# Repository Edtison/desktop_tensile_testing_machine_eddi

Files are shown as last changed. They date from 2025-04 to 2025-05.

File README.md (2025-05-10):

# Desktop Tensile Testing Machine

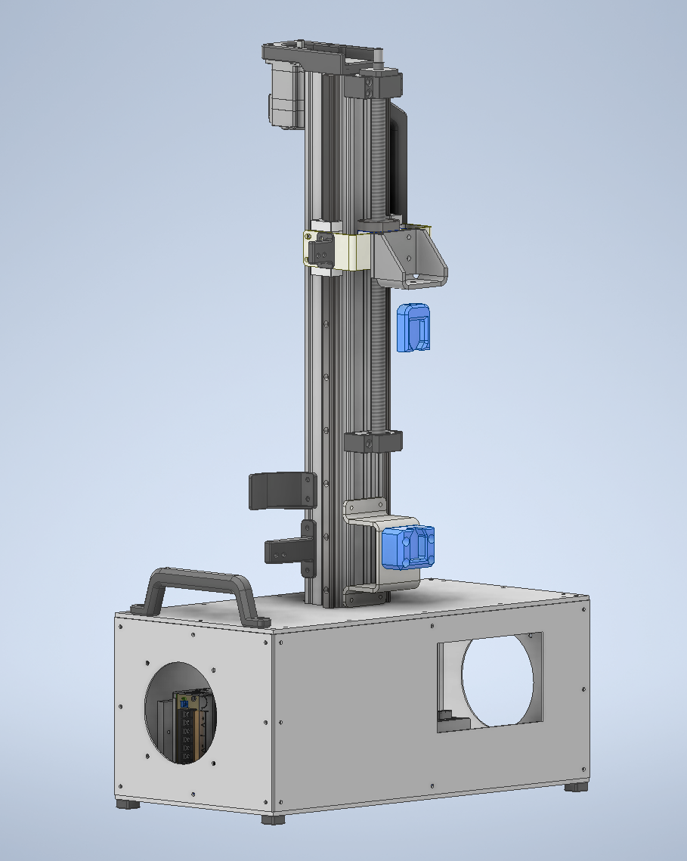
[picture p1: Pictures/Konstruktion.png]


## Overview

The tensile testing machine described here is a fully open-source device designed to determine the mechanical tensile strength of test specimens. At its core, it uses a single-board computer (typically a Raspberry Pi), which, in combination with a load cell and an HX711 amplifier, performs precise force measurements. A bipolar stepper motor module ensures defined positioning and feed control, enabling reproducible loading profiles.
The goal of the project is to provide an affordable and modular testing rig that can be used and further developed by both hobbyists and research laboratories. Control is provided via an intuitive touch GUI (based on ttkbootstrap and tkinter), which visualizes all relevant parameters—test length, feed rate, and force-drop threshold—in real time and automatically saves measurement data to CSV logs.
Thanks to the MIT open-source license, the entire source code is freely available on GitHub. The modular architecture and clear interfaces allow for customization, extensions, and the integration of additional sensors or actuators. This makes the tensile tester a flexible platform for material testing, educational purposes, and DIY projects.

Please Note: a good part of this project is made in german language

If you want to contribute please let me know 

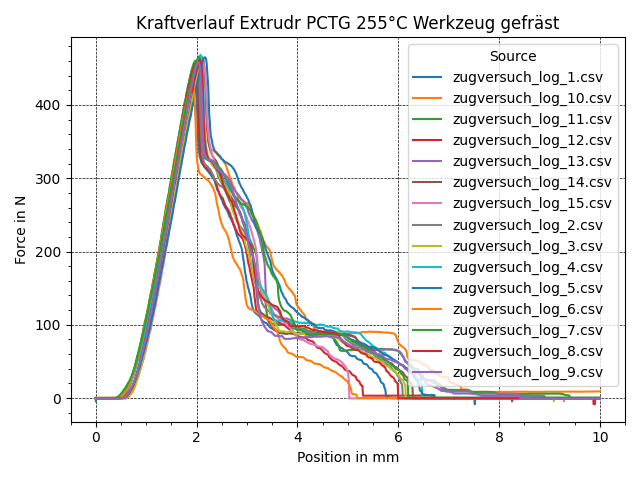
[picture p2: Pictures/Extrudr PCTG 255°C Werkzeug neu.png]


## Features

- **Precise Force Measurement**  
  Load cell with HX711 amplifier, tare & calibration routines.
- **Stepper Motor Control**  
  Configurable pull‑rate, travel distance, and emergency stop on force drop.
- **Intuitive Touch GUI**  
  Built with `ttkbootstrap` + `tkinter` for live feedback and parameter adjustment.
- **Automatic Logging**  
  CSV log files with position vs. force data, auto‑incrementing filenames.

## Requirements

- **Hardware**  
  - Raspberry Pi (5)  
  - HX711 load cell amplifier + load cell  
  - Bipolar stepper motor (Nema 23) + driver (enable, dir, step pins) (3,3V compatible) 
- **Software**  
  - Python 3.11 < 
  - MicroPython (for MCU variant)  
  - `gpiozero`  
  - `ttkbootstrap`  
  - `tkinter`

## Samples 

For good compareable data i would suggest you use the "sample typ cw" from this ropository. The infill should be 100%, the infill pattern rectalinear, with 2 wall loops. This will enshure you will get a homogeneous as possible infill as seen on th picture. Theres als a .3mf data in this repository you could use in Orca Slicer or "Anycubic next" Slicer. The sample contour is fetched from the ISO 20753, also to have good comparable data.

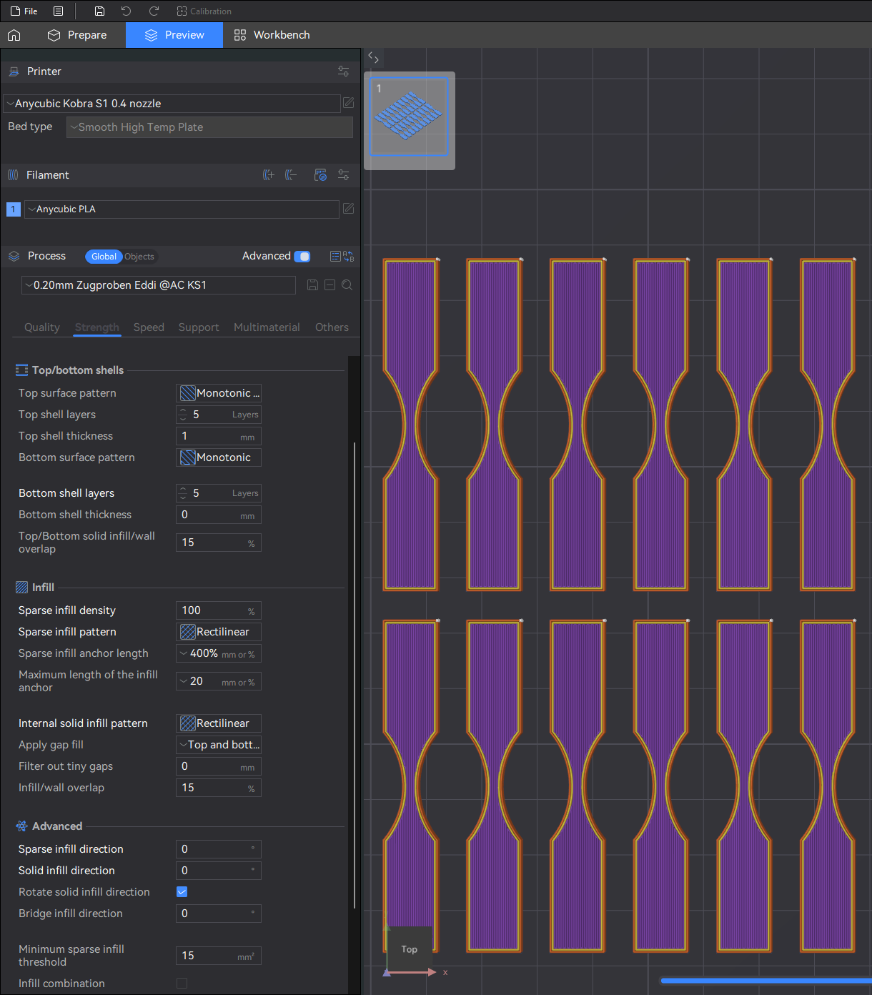
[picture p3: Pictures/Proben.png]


## Addition Milled Sample Holder (10.05.2025)

For a more consistant i've ordered a new sample holder milled from EN-AW7075 aluminum.
You will find the data to that in 3D files and CNC Milled Tool for Type CW

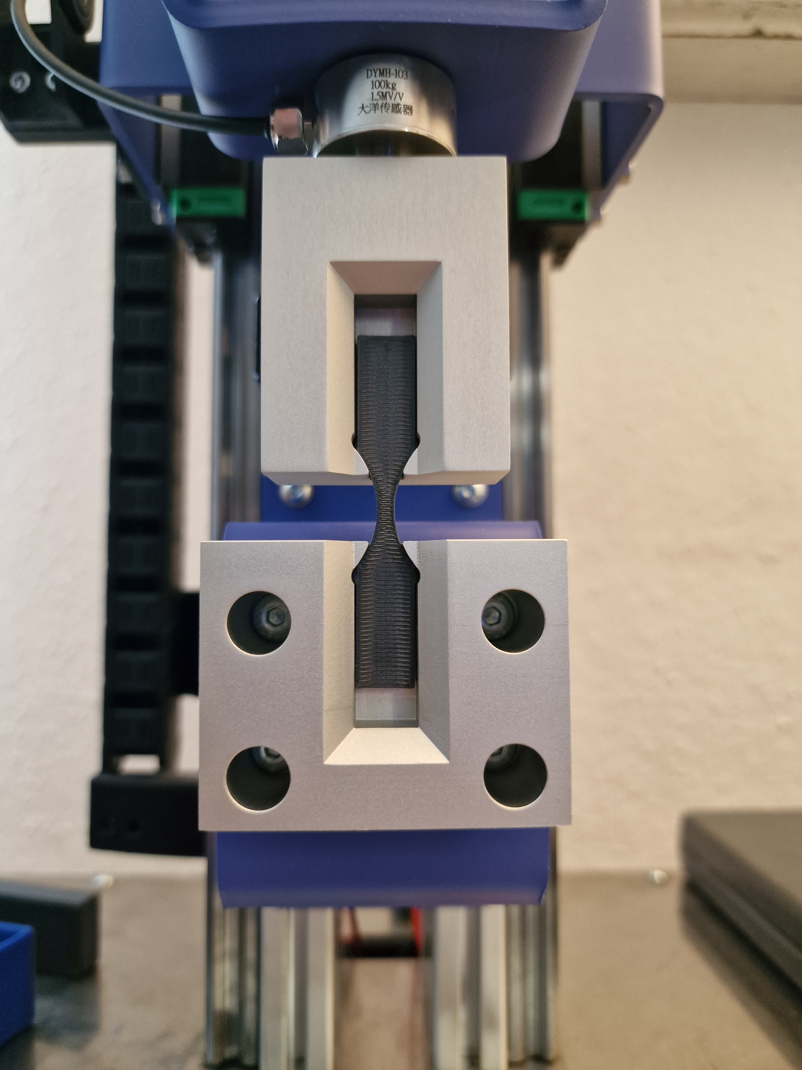
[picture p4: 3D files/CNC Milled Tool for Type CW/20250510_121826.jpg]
milled sample holder


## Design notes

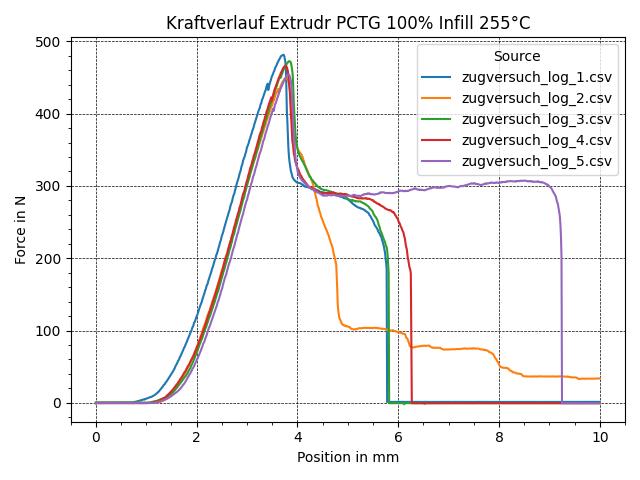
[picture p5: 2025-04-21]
Pictures/Diagram_Extrudr_PCTG.jpeg

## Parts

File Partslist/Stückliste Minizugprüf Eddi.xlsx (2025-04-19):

Stückliste Minizugprüfmaschine Eddi
ID | Bezeichnung | Shop / Firma | Menge | Preis Stk | Preis ges (N) | Preis ges (B) | Link
 | Profile
1 | Aluprofil 20x20 I-Typ Nut5 200mm | Motedis | 4 |  | 11.22 € | 13.46 €
2 | Aluprofil 20x20 I-Typ Nut5 210mm | Motedis | 4 |  | 3.38 € | 4.06 €
3 | Aluprofil 20x20 I-Typ Nut5 460mm | Motedis | 4 |  | 7.41 € | 8.89 €
4 | Aluprofil 20x60 I-Typ Nut5 600mm | Motedis | 2 |  | 27.07 € | 32.48 €
5 | Winkel 20 I-Typ Nut 5 | Motedis | 30 |  | 8.10 € | 9.72 €
6 | Nutenstein I Typ 5 M4 | Motedis | 100 |  | 17.00 € | 20.40 €
7 | Nutenstein mit Steg I-Typ Nut 5 [M5] | Motedis | 70 |  | 12.15 € | 14.58 €
8 | Energiekette 15x15 - 1m | Motedis | 1 |  | 3.80 € | 4.56 €
 | Linearbewegung
9 | 2Stück HGR20-600mm Führungsschiene mit 4Stück Hohe Präzision HGH20CA Linearlager Lagerblock, CNC Teile für 3D Drucker (linearführung HGR20 600mm) | Amazon | 1 |  |  | 48.46 € | https://www.amazon.de/dp/B09JFX8992?ref_=ppx_hzsearch_conn_dt_b_fed_asin_title_1
10 | SFU1605 Kugelumlaufspindel 450mm Gewindespindel Edelstahl Kugelumlaufspindel mit BK12/BF12 Unterstützung, | Amazon | 1 |  |  | 36.31 € | https://www.amazon.de/dp/B0B6RJPQDZ?ref_=ppx_hzsearch_conn_dt_b_fed_asin_title_1&th=1
 | Motor + Treiber
11 | 1 x 1 Achsen Schrittmotor CNC Kit 3,0Nm(425oz.in) Nema 23 Schrittmotor und Treiber | Stepperonline | 1 |  |  | 53.83 €
 | Elektronik
12 | 24V 5A 120W DC Schaltnetzteil AC 100V/240V auf DC-24V Netzteil | Amazon | 1 |  |  | 15.12 € | https://www.amazon.de/dp/B0BX2GF5QY?ref_=ppx_hzsearch_conn_dt_b_fed_asin_title_4
13 | YIMATEECO Staubfilter PC 120mm Lüfterabdeckungen für Computer-Kühlerlüfter | Amazon | 1 |  |  | 7.04 € | https://www.amazon.de/dp/B0BXJJH1X8?ref_=ppx_hzsearch_conn_dt_b_fed_asin_title_1&th=1
14 | LUCKFOX for Raspberry Pi Screen 7 inch HDMI Touchscreen for Raspberry Pi 5 | Amazon | 1 |  |  | 60.49 € | https://www.amazon.de/dp/B0CGNH5G68?ref_=ppx_hzsearch_conn_dt_b_fed_asin_title_1
15 | RPi GPIO Breakout-Erweiterungskarte + Flachbandkabel | Amazon | 1 |  |  | 5.64 € | https://www.amazon.de/dp/B07KB3JF68?ref_=ppx_hzsearch_conn_dt_b_fed_asin_title_3
16 | Raspberry Pi 5 4gb Ram | Berrybase | 1 |  |  | 65.90 € | https://www.berrybase.at/raspberry-pi-5-4gb-ram
17 | Raspberry Pi5 active Cooler | Berrybase | 1 |  |  | 5.70 € | https://www.berrybase.at/raspberry-pi-active-cooler-luefter-fuer-raspberry-pi-5
18 | HX711 Wägezelle 24-Bit-A/D-Wandlerchip für elektronische Präzisionswaage | Amazon | 1 |  |  | 7.04 € | https://www.amazon.de/dp/B07MY2PBY4?ref_=ppx_hzsearch_conn_dt_b_fed_asin_title_1
19 | DYMH 103 Mikro-Miniatur-Wägezelle Wägezelle Wägesensor Zugstangen-Druckspannungssensor (Bereich 0~100kg) | Amazon | 1 |  |  | 41.38 € | https://www.amazon.de/Mikro-Miniatur-W%C3%A4gezelle-W%C3%A4gezelle-W%C3%A4gesensor-Zugstangen-Druckspannungssensor-Bereich/dp/B0C3JFGVHX?__mk_de_DE=%C3%85M%C3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
20 | REV Standard, Feuchtraumsteckdose, Aufputz, grau | Amazon | 1 |  |  | 4.52 € | https://www.amazon.de/REV-Ritter-10216-Steckdose-Standard/dp/B00V3OI8YW
21 | 3 Stück Kaltgeräte Einbau-Stecker 220-250V/ 10A | Amazon | 1 | 10.07 € |  | 3.36 € | https://www.amazon.de/dp/B07T5D39R3?ref_=ppx_hzsearch_conn_dt_b_fed_asin_title_1
 | Blechteile
22 | Bodenplatte | Mon-Tec | 1 |  |  | 26.64 €
23 | Deckplatte | Mon-Tec | 1 |  |  | 29.78 €
24 | Festlagerblech | Mon-Tec | 1 |  |  | 29.89 €
25 | Führungswinkel | Mon-Tec | 2 | 11.35 € |  | 22.70 €
26 | Zugwinkel | Mon-Tec | 1 |  |  | 34.15 €
27 | Seitenblech | Mon-Tec | 2 | 15.00 € |  | 30.00 €
28 | Frontblech | Mon-Tec | 1 |  |  | 25.00 €
29 | Rückblech | Mon-Tec | 1 |  |  | 25.00 €
 | Schrauben
30 | M4x8 Inbus | Schraubenking | 100 |  |  | 2.45 €
31 | M4x10 Linsenflachkopf | Schraubenking | 100 |  |  | 2.64 €
32 | M5x12 Linsenflachkopf | Schraubenking | 30 |  |  | 0.90 €
33 | M5x16 Inbus | Schraubenking | 20 |  |  | 0.20 €
34 | Unterlegscheiben M4 | Schraubenking | 100 |  |  | 1.06 €
35 | Unterlegscheiben M5 | Schraubenking | 10 |  |  | 0.30 €
36 | M6 Mutter | Schraubenking | 1 |  |  | 0.00 €
 |  |  |  |  | Summe | 693.65 €
ID | 3D-Druck Teile | Menge
1 | Motorhalter Nema 23 | 1
2 | Halterung Kabelschlepp fahrend | 1
3 | Halterung Kabelschlepp fix | 1
4 | Tragegriff | 1
5 | Tragegriff seite | 1
6 | Auflage Kabelschlepp | 1
7 | Fliegender Probenhalter (auch als Frästeil möglich) | 1
8 | Probenhalter fix (auch als Frästeil möglich) | 1

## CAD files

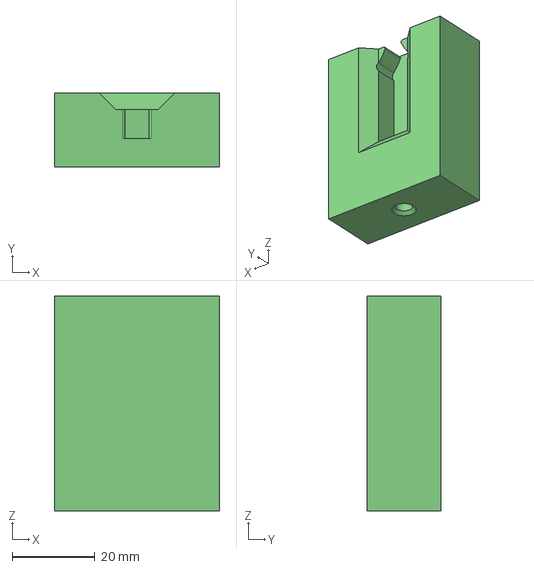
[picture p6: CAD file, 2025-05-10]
3D files/CNC Milled Tool for Type CW/Sample Holder flying CW.stp
40.0 x 18.0 x 52.0 mm

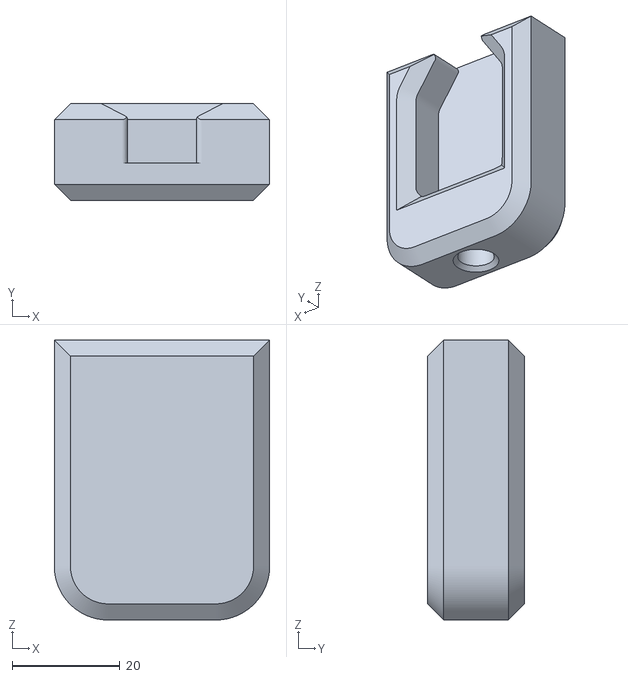
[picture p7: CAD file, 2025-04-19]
3D files/STL for printing/Fliegender Probenhalter.stl
40.0 x 18.0 x 52.0

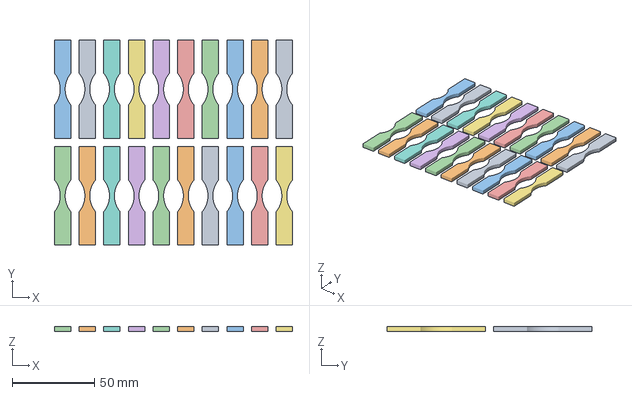
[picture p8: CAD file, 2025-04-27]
sample typ CW/sample Typ CW.3mf
145.0 x 125.0 x 3.00 mm
Zugprobe Typ CW.stl x 20

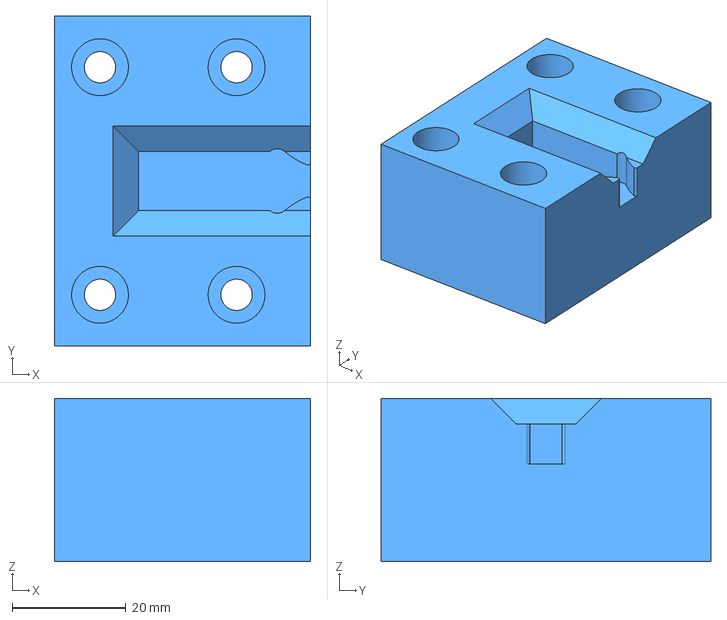
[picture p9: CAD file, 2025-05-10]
3D files/CNC Milled Tool for Type CW/Sample holder fixed CW.stp
45.0 x 58.0 x 28.7 mm

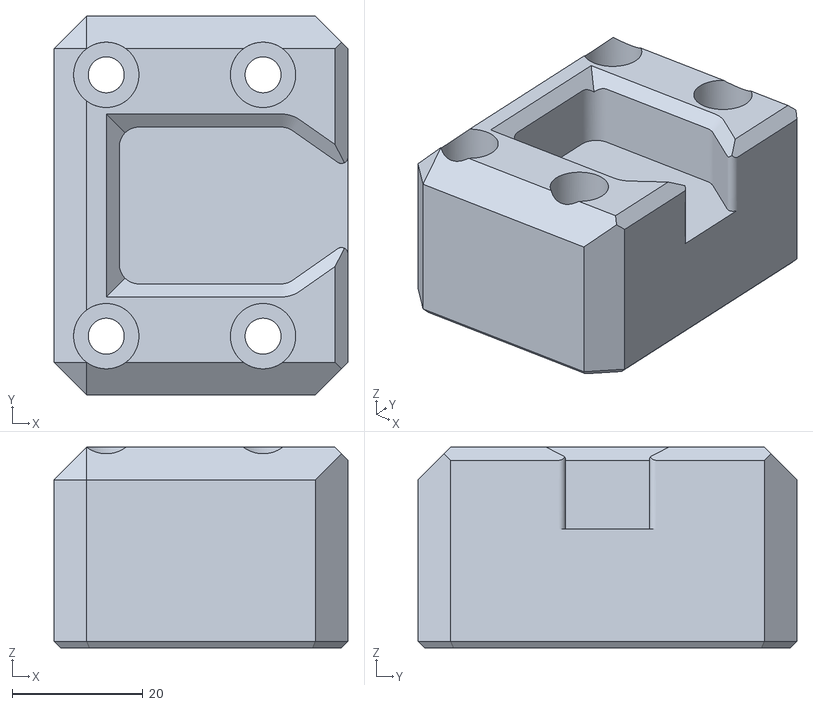
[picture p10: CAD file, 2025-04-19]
3D files/STL for printing/Probenhalter Fix.stl
45.0 x 58.0 x 30.7

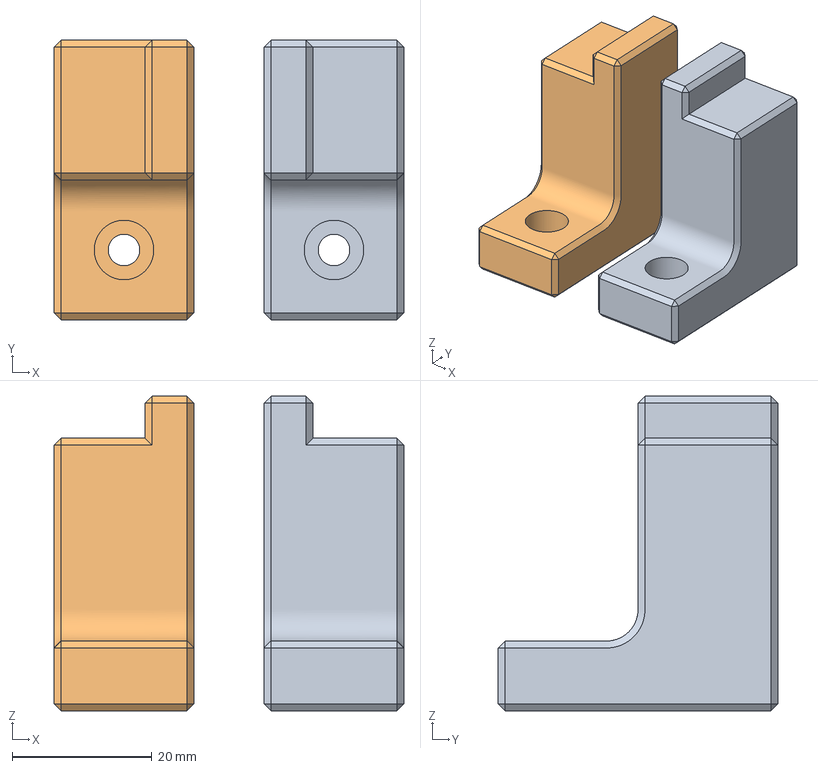
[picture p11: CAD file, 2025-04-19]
3D files/STL for printing/Bildschirm Steher.3mf
50.0 x 40.0 x 45.0 mm
Bildschirm Steher.stl x 2

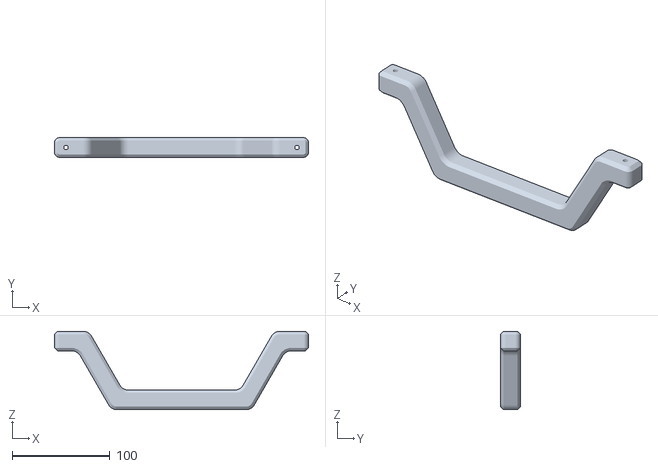
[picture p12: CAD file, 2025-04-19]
3D files/STL for printing/Tragegriff.stl
259.3 x 20.0 x 80.0

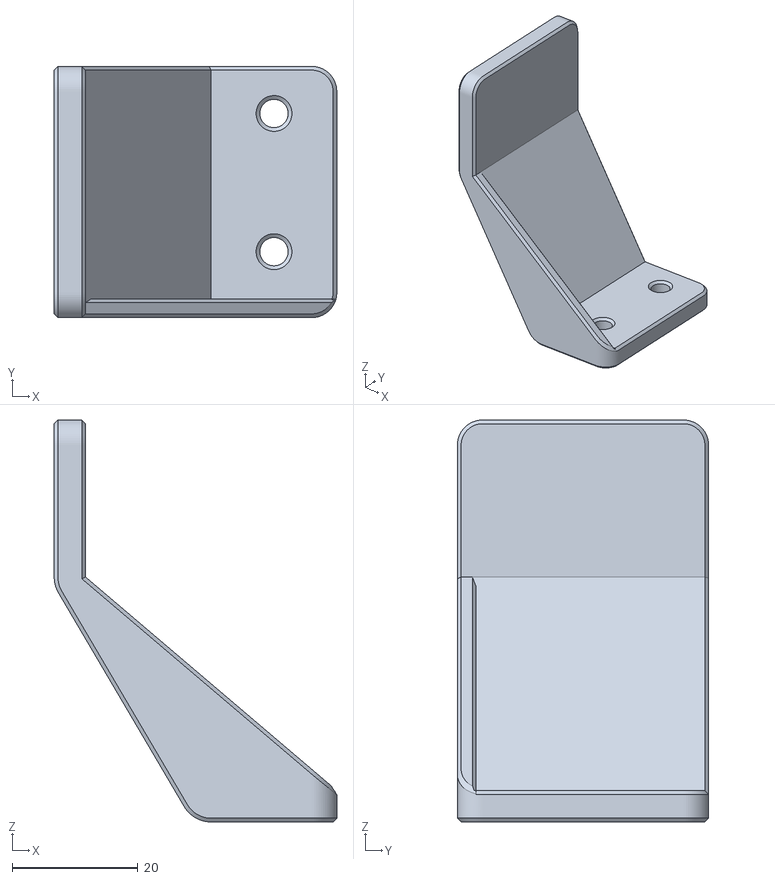
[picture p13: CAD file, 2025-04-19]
3D files/STL for printing/Auflage Kabelschlepp.stl
45.0 x 40.0 x 64.0

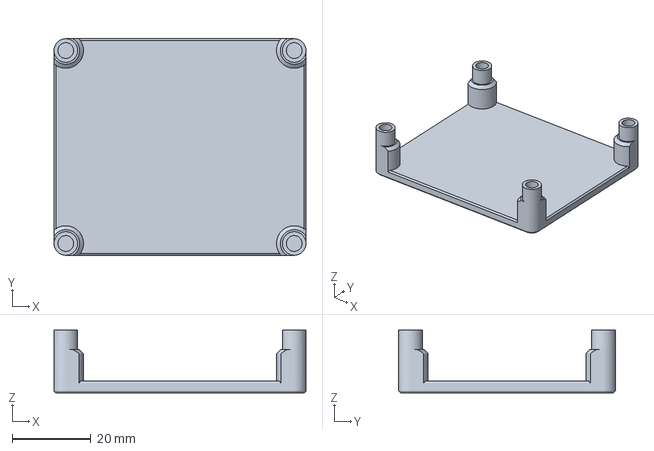
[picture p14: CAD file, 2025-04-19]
3D files/STL for printing/Raspberry Halterung.3mf
64.0 x 55.0 x 16.0 mm

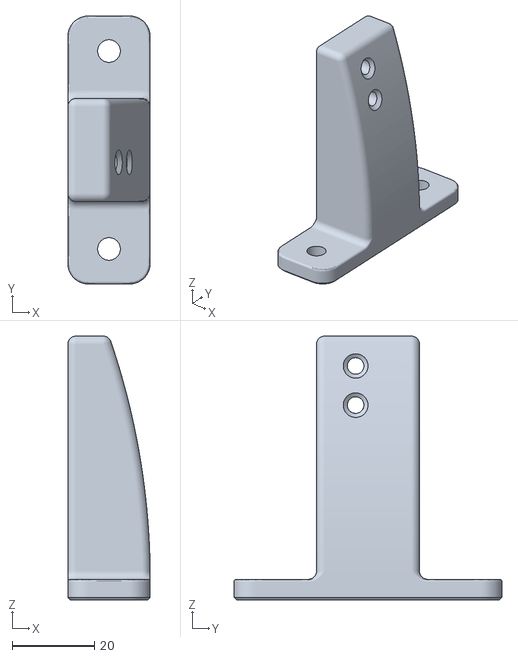
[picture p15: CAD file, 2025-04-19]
3D files/STL for printing/Hakterung Kabelschlett fix.stl
20.0 x 65.0 x 64.0

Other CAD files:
3D files/Production Drawings/Führungswinkel.dwg
3D files/Production Drawings/Seitenbleche.dwg
3D files/Production Drawings/Festlagerblech.dwg
3D files/Production Drawings/Frontblech.dwg
3D files/Production Drawings/Deckplatte.dwg
3D files/Production Drawings/Zugwinkel.dwg
3D files/Production Drawings/Bodenplatte.dwg
3D files/Production Drawings/Rückblech Zugprüf.dwg
3D files/STL for printing/Bildschirm Halterung.stl
3D files/STL for printing/Bildschirm Steher.stl
3D files/STL for printing/Halterung Kabelschlepp fahrend.stl
3D files/STL for printing/Halterung Klemmen 4Fach.stl
3D files/STL for printing/Kabelklipp.stl
3D files/STL for printing/Klammer_USB.stl
3D files/STL for printing/Motorhalter_Nema23.stl
3D files/STL for printing/Raspberry Halterung.stl
3D files/STL for printing/Schienen_Montierhilfe.3mf
3D files/STL for printing/Schienen_Montierhilfe.stl
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

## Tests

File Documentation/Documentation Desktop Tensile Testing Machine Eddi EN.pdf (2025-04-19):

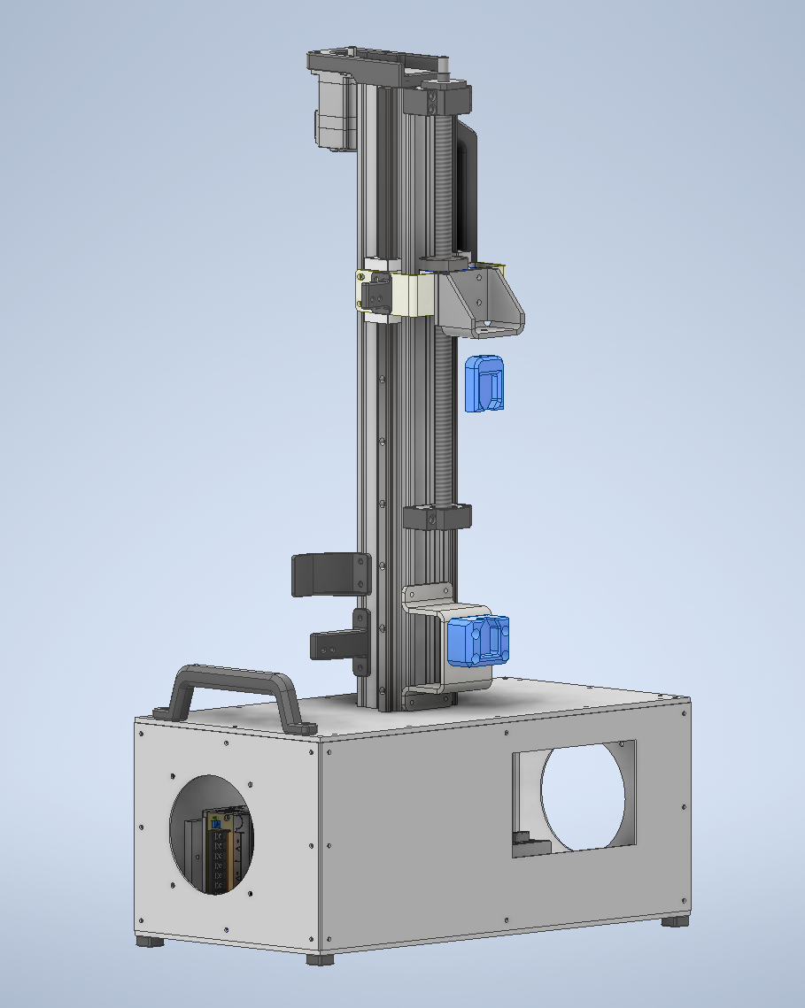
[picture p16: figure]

## Contents

1 Introduction | 3
2 Bill of Materials Electronics / Mechanics | 4
3 3D-Printed Parts | 5
4 Mechanics Notes and Assembly | 6
5 Electrical Notes and Assembly | 6
5.1 Circuit Diagram | | 8
6 Software Overview | 9
6.1 Component Overview | | 9
7 Installation | 9
7.1 Clone the Repository | | 9
7.2 Install Dependencies | | 9
8 Conguration & Calibration | 9
9 Usage | 10
9.1 Starting the Application | 10
9.2 Operation | 10
10 License | 10

## 1 Introduction

The tensile testing machine described here is a fully open-source device for determining the mechanical tensile strength of test specimens. At its core is a single-board computer (typically a Raspberry Pi), which, together with a load cell and an HX711 amplier, performs precise force measurements. A bipolar stepper-motor module handles the dened positioning and feed control, enabling reproducible loading proles.

The goal of the project is to provide an aordable, modular test rig that can be used and further developed by hobbyists as well as research laboratories. Control is provided via an intuitive touch GUI (using ttkbootstrap and tkinter), which visualizes all relevant parameterstest length, feed rate, force-drop thresholdin real time and automatically saves measurement data to CSV logs through programmable routines.

Thanks to the MIT open-source license, the entire source code is freely available on GitHub. The modular architecture and clear interfaces facilitate customization, extension, and integration of additional sensors or actuators. This makes the tensile tester a exible platform for material testing, educational purposes, and DIY projects.

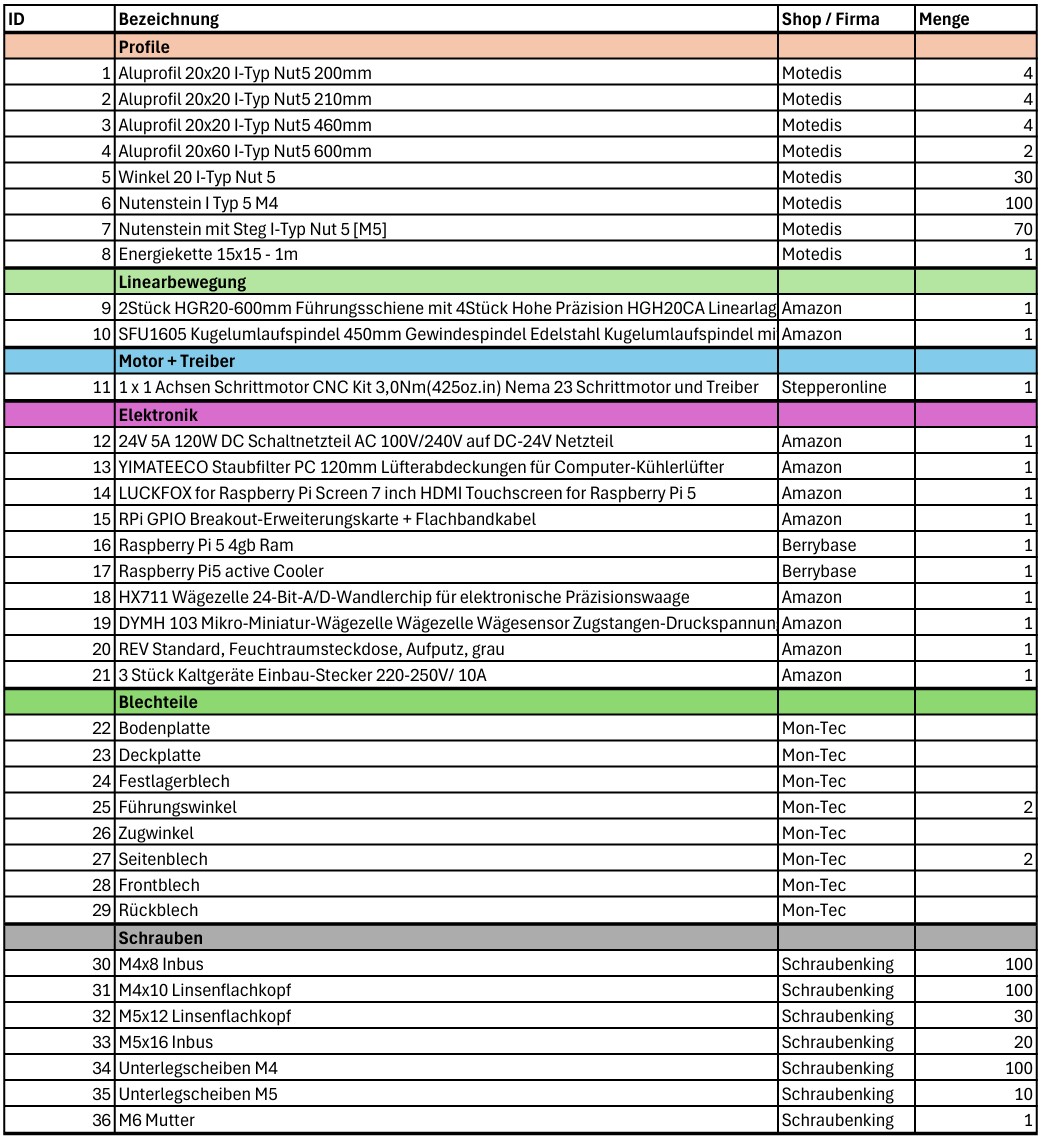
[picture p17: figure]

## 3 3D-Printed Parts

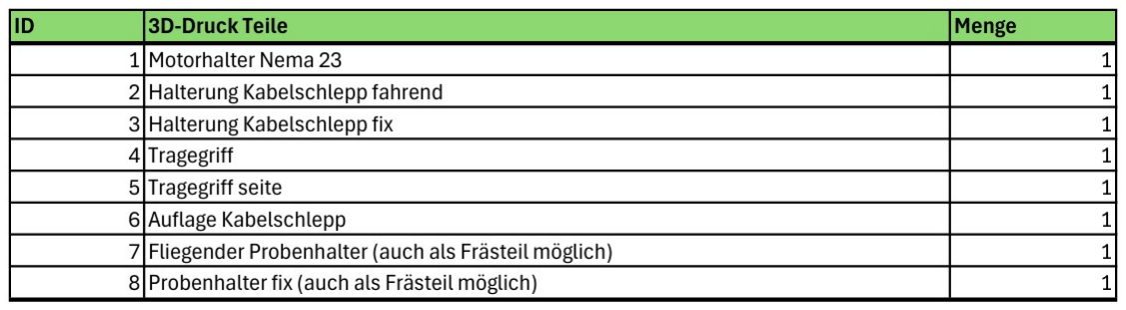
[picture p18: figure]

Figure 2: List of 3D-Printed Parts

For part of the tensile tester, 3D-printed components were used (see list). In the original version, PCTG was employed. In general, the parts are designed for brass threaded inserts, which can be obtained from Rutex 3D.

An **inll of 50%** is recommended for these parts!

If the sample holders are also 3D-printed, **PCTG** or **ASA** is advised. A minimum of **5 wall loops** and at least **70% inll** are recommended.
A STEP le for the sample holders (for milling) is also available. In general, a milled aluminum or steel part is preferable to a 3D-printed plastic one.

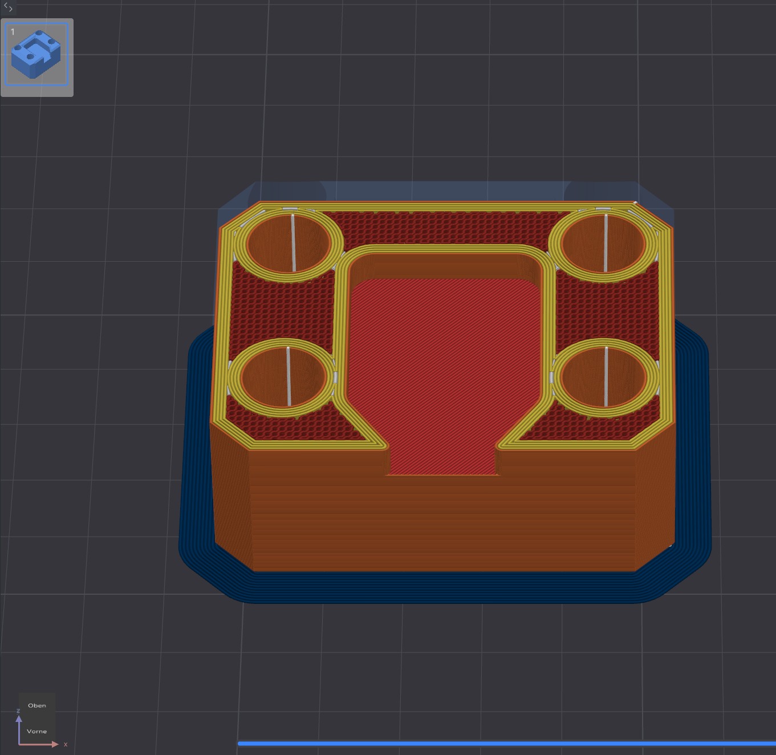
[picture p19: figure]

Figure 3: Fixed Sample Holder as 3D Print

## 4 Mechanics Notes and Assembly

The sheet-metal parts to be ordered are designed for laser cutting and subsequent bending. Structural steel (S235 / S355) is specied. If tensile forces exceed 2kN, a more robust design in stronger steelor even a machined partshould be used.

Pulleys and the timing belt are not included in the bill of materials. Order these to match the chosen motor and ball screw. For up to 2kN, a 6mm GT2 belt with berglass reinforcement is sucient; above that, a wider belt system is recommended.

Mechanical assembly should follow the Assembly step. The 3D-printed parts include alignment aids for both the linear rails and the ball screw. It is critical that the linear guides and ball screw are precisely parallelsmall misalignments can signicantly increase motor load and lead to lost steps. Use a dial indicator for accurate alignment.

## 5 Electrical Notes and Assembly

Warning: When working on the electrical assembly, please observe all general safety guidelines for handling mains voltage. Mains voltage (230V) can cause serious injury or equipment damage if handled incorrectly!

The base plate is intended for self-tapping screws, so all electronics can be mounted this way. Ensure the base plate is grounded via the power supplyfailure to do so may damage the electronics over time.

Keep the 230V and 24V circuits as separate as possible. If the mains lines are routed too close to sensor or control cables, interference or errors may occur, compromising measurement accuracy.

The Raspberry Pi 5and all other Raspberry Pi modelsprovides 3.3V on its GPIO pins. When ordering the motor driver, verify that its PUL/EN/DIR inputs tolerate a 3.3V high-level signal. The StepperOnline driver listed has been tested and works; alternatively, a TMC2209 on a breakout board may be used.

Important: Use an HX711 board rated for an 80Hz sampling rate!

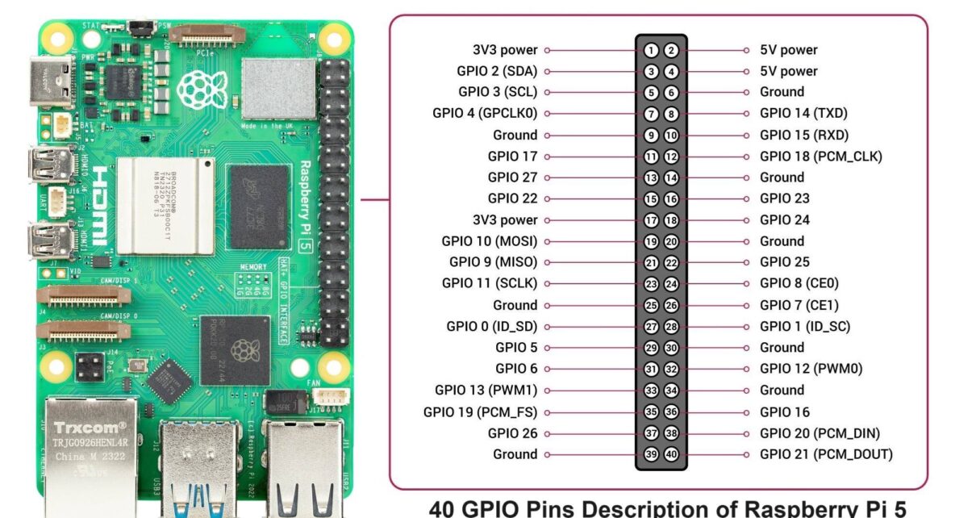
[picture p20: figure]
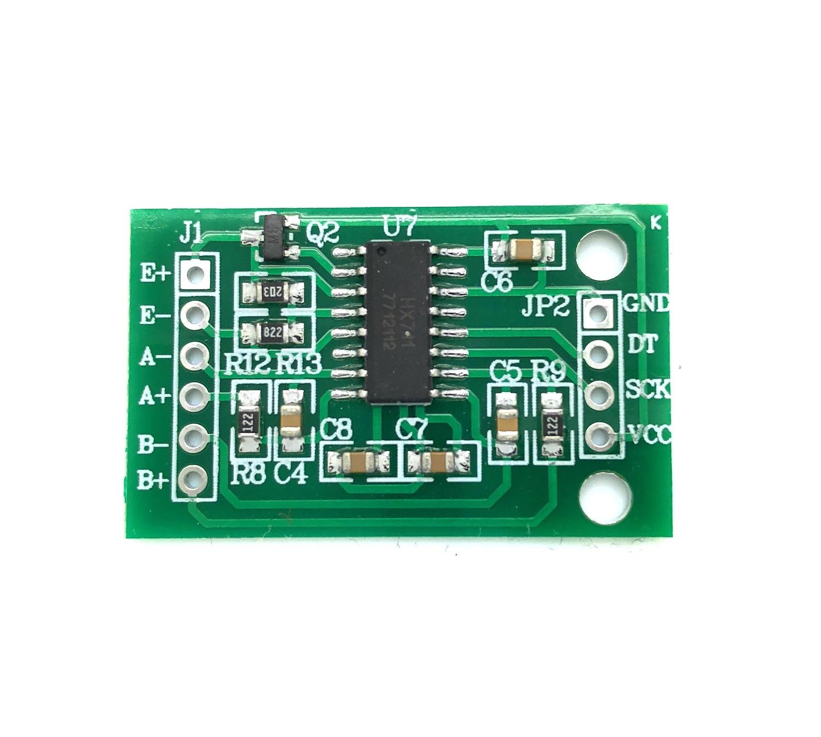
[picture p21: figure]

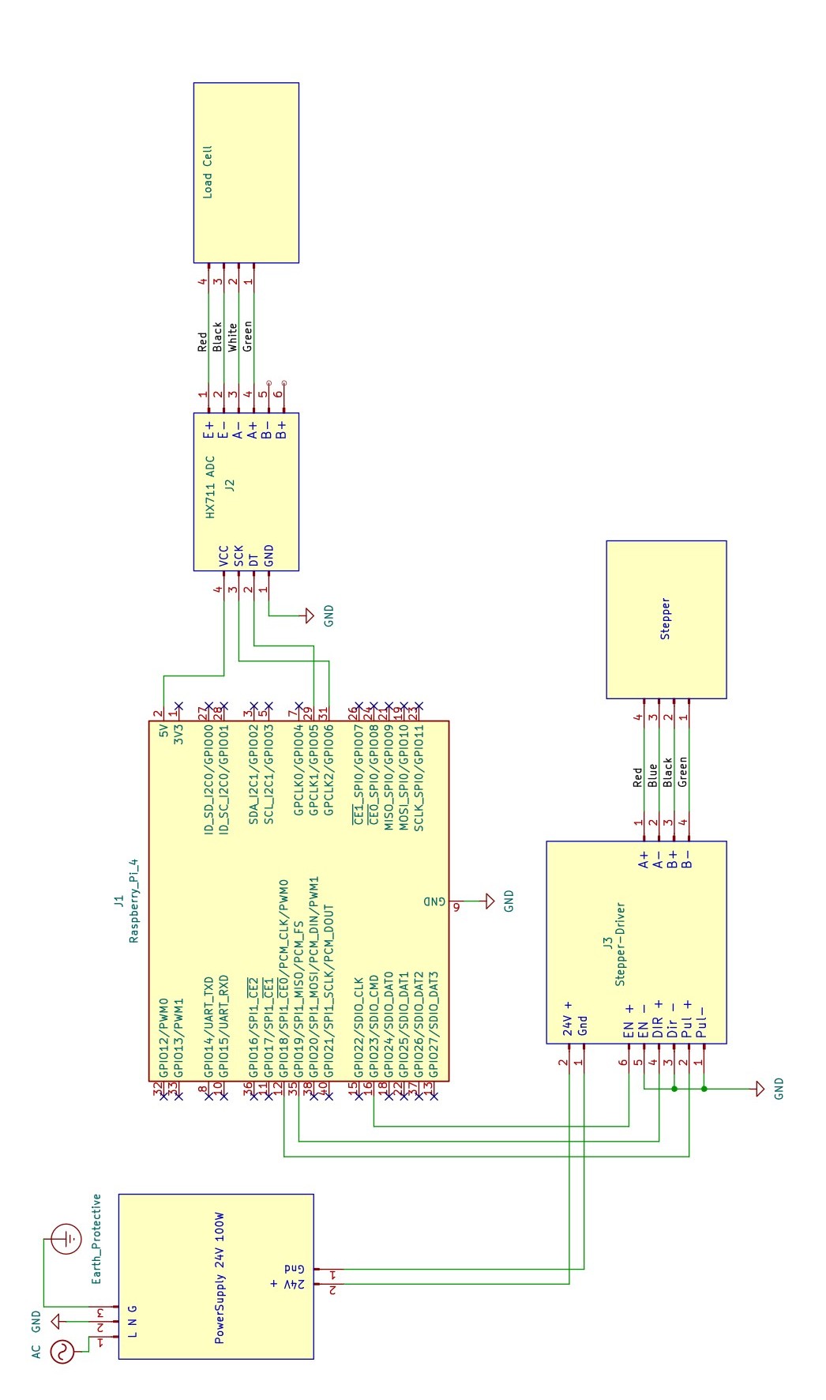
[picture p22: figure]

## 6 Software Overview

### 6.1 Component Overview

| Programming Language: Python 3
| Libraries: gpiozero (install via pip) ttkbootstrap + tkinter (install via pip) Module HX711.py (included in repository)
| Scripts: HX711.py: Load-cell reading and calibration ZP_Final2.py: Main GUI and logic

## 7 Installation

### 7.1 Clone the Repository

1 | https :// github . com / Edtison / desktop_tensile_testing_machine_eddi Listing 1: Clone the Repository

### 7.2 Install Dependencies

1 | pip install gpiozero ttkbootstrap tk Listing 2: Install Python Packages

## 8 Conguration & Calibration

1. Open HX711.py and run main() to determine the reference_unit value. Weigh two
| known masses and adjust the value so that the displayed force is correct.
2. In ZP_Final2.py, adjust the force variable accordingly.

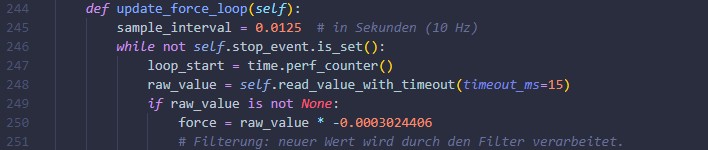
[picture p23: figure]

Figure 7: Reference Value for Force in ZP Final2

## 9 Usage

### 9.1 Starting the Application

1 | python ZP_Final2 . py Listing 3: Start the GUI

Run either from a terminal or via Thonny.

### 9.2 Operation

| Tare: Zero the scale.
| Feed & Test Length: Adjust with the buttons.
| Prozess Starten: Begin the measurement run.
| Pos. Nullsetzen: Sets the current position to 0.
| Zurück zu 0 Position: Moves the crosshead back to 0mm.
| Log les are saved in logs/.
| Log base denes the lename prex before the index.

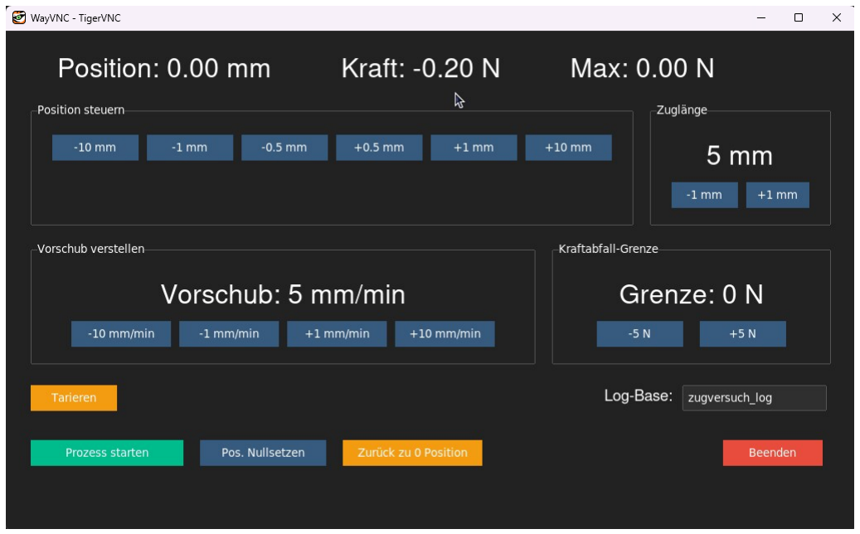
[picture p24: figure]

Figure 8: GUI of ZP Final2

## 10 License

This project is licensed under the MIT License. See LICENSE.

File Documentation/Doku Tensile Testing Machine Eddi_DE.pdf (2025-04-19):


## Inhaltsverzeichnis

1 Einführung | 3
2 Stückliste Elektronik / Mechanik | 4
3 Teile 3D-Druck | 5
4 Mechanik - Anmerkungen und Montage | 6
5 Elektrik - Anmerkungen und Montage | 6
5.1 Schaltplan | | 8
6 Softwareübersicht | 9
6.1 Übersicht der Komponenten | | 9
7 Installation | 9
7.1 Repository klonen | | 9
7.2 Abhängigkeiten installieren | | 9
8 Konguration & Kalibrierung | 9
9 Nutzung | 10
9.1 Starten der Anwendung | 10
9.2 Bedienung | 10
10 Lizenz | 10

## 1 Einführung

Die hier beschriebene Zugprüfmaschine ist ein vollständig Open-Source entwickeltes Gerät zur Bestimmung mechanischer Zugfestigkeiten von Prüfkörpern. Als Herzstück fungiert ein Einplatinencomputer (typischerweise Raspberry Pi), der in Kombination mit einer Wägezelle und einem HX711-Verstärker präzise Kraftmessungen durchführt. Ein bipolares Schrittmotor-Modul übernimmt die denierte Positionierung und Vorschubsteuerung, sodass reproduzierbare Belastungsprole realisiert werden können.

Ziel des Projekts ist es, eine kostengünstige und modular erweiterbare Prüfanlage bereitzustellen, die sowohl von Hobby-Tüftlern als auch von Forschungslabors genutzt und weiterentwickelt werden kann. Die Steuerung erfolgt über eine intuitiv bedienbare Touch-GUI (mittels ttkbootstrap und tkinter), die alle relevanten Parameter Zuglänge, Vorschubrate, Kraftabfallgrenze in Echtzeit visualisiert und über programmierbare Abläufe automatisch Messdaten in CSV-Logs speichert.

Dank der Open-Source-Lizenzierung (MIT) steht der gesamte Quellcode frei auf GitHub zur Verfügung. Modulbauweise und klare Schnittstellen erleichtern Anpassungen, Erweiterungen und Integration zusätzlicher Sensorik oder Aktorik. Damit wird die Zugprüfmaschine zu einer exiblen Plattform für Materialtests, Lehrzwecke und DIY-Projekte.


## 3 Teile 3D-Druck


Abbildung 2: Liste 3D-Druck Teile

Für einen Teil der Zugprüfmaschine wurden 3D gedruckte Teile verwendet (siehe Liste). Hier wurde in der Ursprungsversion PCTG verwendet. Generell sind die Teile für Messing Gewindeeinsätze Konstruiert. Diese sind von der Firma Rutex 3D erhältlich.

Für die Teile wird ein Inll von 50 empfohlen!

Sollten die Probenhalter auch in 3D-Druck gefertigt werden wird hier PCTG oder ASA empfohlen. Hier wird ein minimum von 5 Wand-Schleifen und ein minimum Inll von 70 geraten.
Es steht auch eine Step Datei für die Probenhalter als Fräsdatei zur Verfügung. Generell wäre ein Frästeil aus Aluminum oder Stahl gegenüber einen 3D-Druck aus Kunststo zu bevorzugen.


Abbildung 3: Probenhalter x als 3D-Druck

## 4 Mechanik - Anmerkungen und Montage

Die Blechteile die zu bestellen sind, wären grundsätzlich für den Laserschnitt und weiterer Biege Verarbeitung konstruiert. Als Material ist hier ein Baustahl (S235 / S355) vorgesehen. Sollten die Zugkräfte 2kN übersteigen wäre eine massivere Ausführung aus stärkeren Stahl, oder gar als Frästeil, zu bevorzugen.

In der Stückliste fehlen die Pulleys und der Zahnriemen. Diese sollten passend für den verwendeten Motor und Kugelumlaufspindel bestellt werden. Bis 2kN reicht eine Ausführung für 6mm GT2 Riemen mit Glasfaserverstärkung! Darüber wird ein breiteres Riemenkonzept empfohlen.

Bei der mechanischen Montage gilt diese Grundsätzlich nach der Assembly-Step durchzuführen. Für die Montierung der Linearschienen und der Kugelumlaufspindel, gibt es bei den 3D Druck Teilen für beides eine Montagehilfe vorhanden. Wichtig hierbei ist das die Linear-Führungen und die Kugelumlaufspinden parallel zueinander sind! Kleine Abweichungen hier wirken sich schnell auf die Aufgewendete Motorarbeit aus und kann zu Step-Verlusten führen! Für eine genaue Ausrichtung sollte eine Messuhr verwendet werden.

## 5 Elektrik - Anmerkungen und Montage

Bei der elektrischen Montage sind bitte die allgemeinen Sicherheitsrichtlinien für das Arbeiten mit Netzspannung zu beachten. Netzspannung (230V) kann bei falscher Verwendung schwere Verletzungen und Sachschäden verursachen!!

Die Bodenplatte ist für die Verwendung von selbst schneidenden Schrauben gedacht. Die gesamte Elektronik kann also mit solchen befestigt werden. Wichtig ist die das Bodenplatte über die Zuleitung geerdet ist. wird dies vergessen, kann die Elektronik über die Zeit schaden nehmen!

230V und 24V Spannungskreise sollten so gut wie möglich voneinander getrennt aufgebaut werden. Wenn die 230V zu nahe an Sensorik Leitungen oder an Steuerungen verlegt wird, kann dies zu Indierenzen oder Fehlern führen welche das Messergebnis beeinträchtigen können!

Der Raspberry Pi5, bzw. auch alle andern Raspberry Pi's haben bei den GPIO Pins 3.3V für die Ausgangsspannung. Es muss also bei der Bestellung des Motortreibers darauf geachtet werden, dass dieser bei den PUL/EN/DIR Pins eine passende High-Level Spannung für die Eingänge hat. Der Treiber von der Firma StepperOnline auf der Stückliste ist auf Funktion getestet. Es ist auch die Verwendung von zum Bsp. eines TMC2209 über ein Breakoutboard möglich.

Wichtig: Beim HX711 ist ein Board mit 80Hz Ausleserate zu verwenden!!



## 6 Softwareübersicht

### 6.1 Übersicht der Komponenten

| Programmiersprache: Python 3
| Bibliotheken: gpiozero (über pip zu installieren) ttkbootstrap + tkinter (über pip zu installieren) Modul HX711.py (in Repository)
| Skripts:
| HX711.py: Auslesung und Kalibrierung der Wägezelle
| ZP_Final2.py: Haupt-GUI und Logik

## 7 Installation

### 7.1 Repository klonen

1 | https :// github . com / Edtison / desktop_tensile_testing_machine_eddi
| Listing 1: Klone das Repository

### 7.2 Abhängigkeiten installieren

1 | pip install gpiozero ttkbootstrap tk
| Listing 2: Installiere Python-Pakete

## 8 Konguration & Kalibrierung

1. Önen Sie HX711.py und starten Sie main(), um den reference_unit-Wert zu er-
| mitteln. Messen Sie zwei verschiedene Gewichte und passen die den Wer so an das die Korrekte Kraft angezeigt wird
2. Passen Sie ebenfalls in ZP_Final2.py den Wert bei der Variable force an.


Abbildung 7: ZP Final2 force reference value

## 9 Nutzung

### 9.1 Starten der Anwendung

1 | python ZP_Final2 . py Listing 3: Starte die GUI

Entweder über Terminal oder Thonny.

### 9.2 Bedienung

| Tare: Waage nullen.
| Vorschub & Zuglänge: Mit Buttons einstellen.
| Prozess starten: Messlauf starten.
| Pos. Nullsetzen: Setzt die Aktuelle Position auf 0
| Zurück zu 0 Position: Fährt die Traverse wieder auf 0mm
| Logles werden in logs/ abgelegt.
| Log-Base gibt den Namen des Logles vorm Index vor.


Abbildung 8: GUI ZP Final2

## 10 Lizenz

Dieses Projekt steht unter der MIT-Lizenz. Siehe LICENSE.

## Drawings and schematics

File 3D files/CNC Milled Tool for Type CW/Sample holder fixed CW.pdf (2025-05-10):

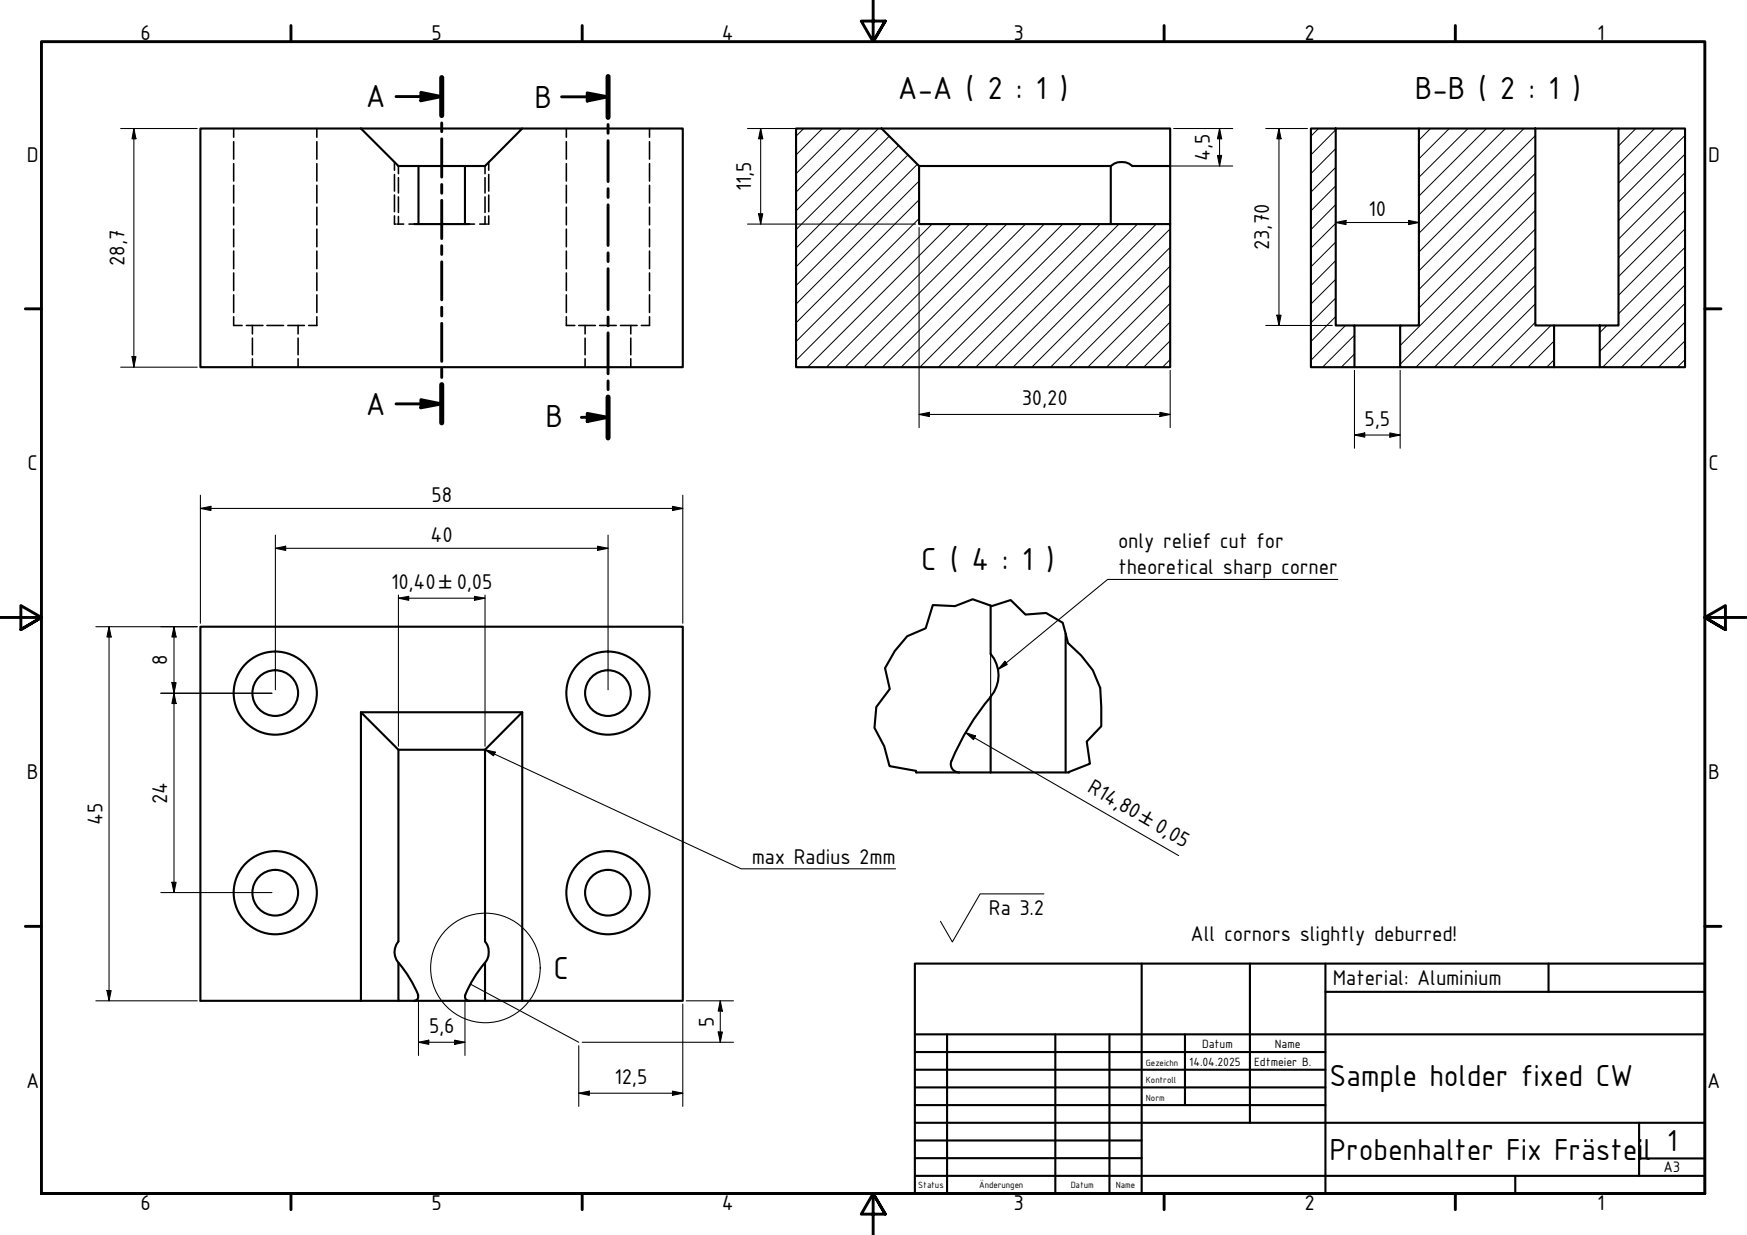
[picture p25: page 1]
max Radius 2mm; Material: Aluminium

only relief cut for
theoretical sharp corner

All cornors slightly deburred!

Datum | Name | Sample holder fixed CW

Gezeichn | 14.04.2025 | Edtmeier B.

Kontroll

Norm

Probenhalter Fix Frsteil

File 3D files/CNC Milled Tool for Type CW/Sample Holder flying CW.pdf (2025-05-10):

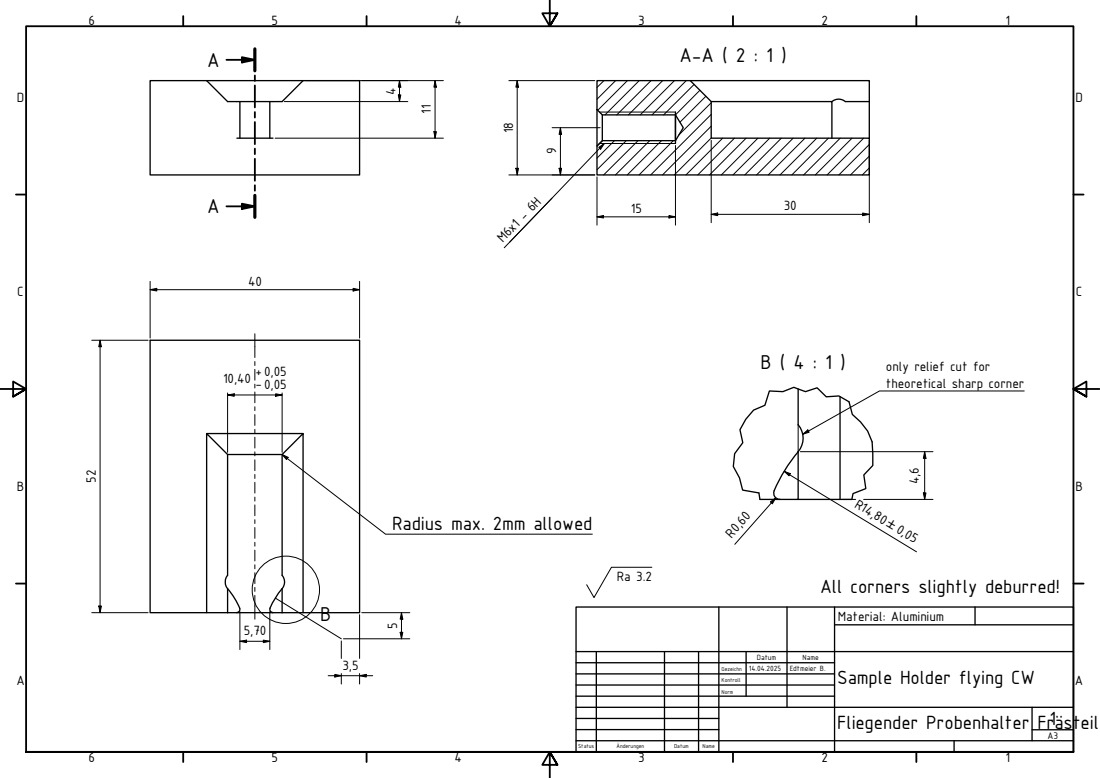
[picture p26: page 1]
Material: Aluminium

only relief cut for
theoretical sharp corner

Radius max. 2mm allowed

All corners slightly deburred!

Datum | Name | Sample Holder flying CW

Gezeichn | 14.04.2025 | Edtmeier B.

Kontroll

Norm

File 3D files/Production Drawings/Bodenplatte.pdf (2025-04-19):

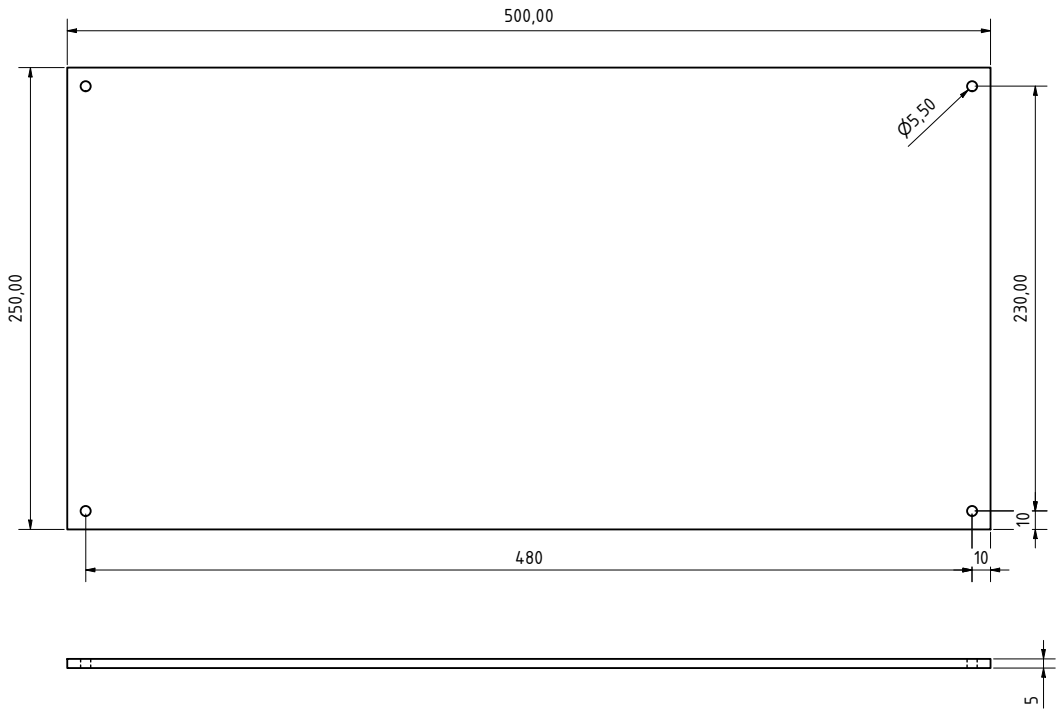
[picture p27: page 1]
Material: Alu

Datum | Name | Bodenplatte

Gezeichn | 09.03.2025 | Edtmeier B.

Kontroll

Norm

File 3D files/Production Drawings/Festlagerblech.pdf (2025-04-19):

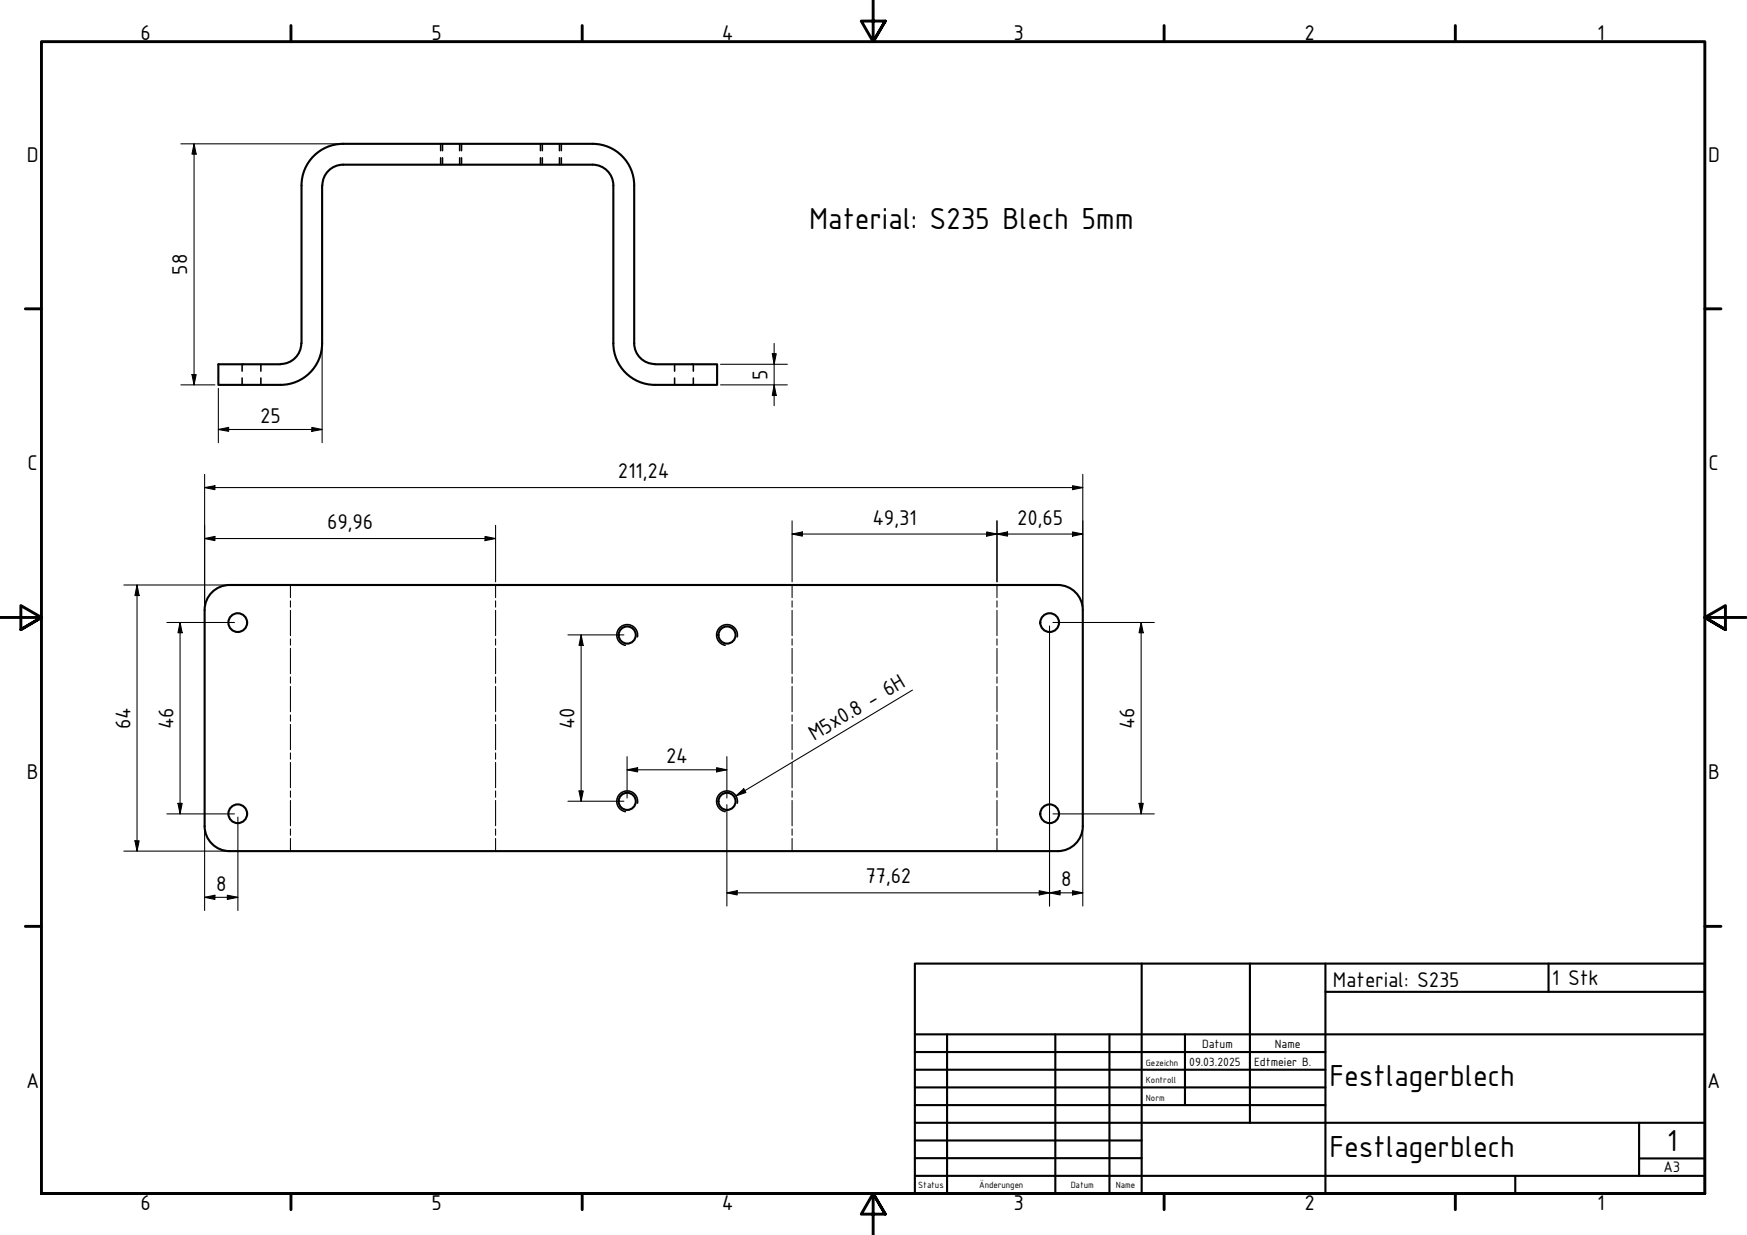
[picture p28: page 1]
Material: S235; Material: S235 Blech 5mm; 1 Stk

Datum | Name | Festlagerblech

Gezeichn | 09.03.2025 | Edtmeier B.

Kontroll

Norm

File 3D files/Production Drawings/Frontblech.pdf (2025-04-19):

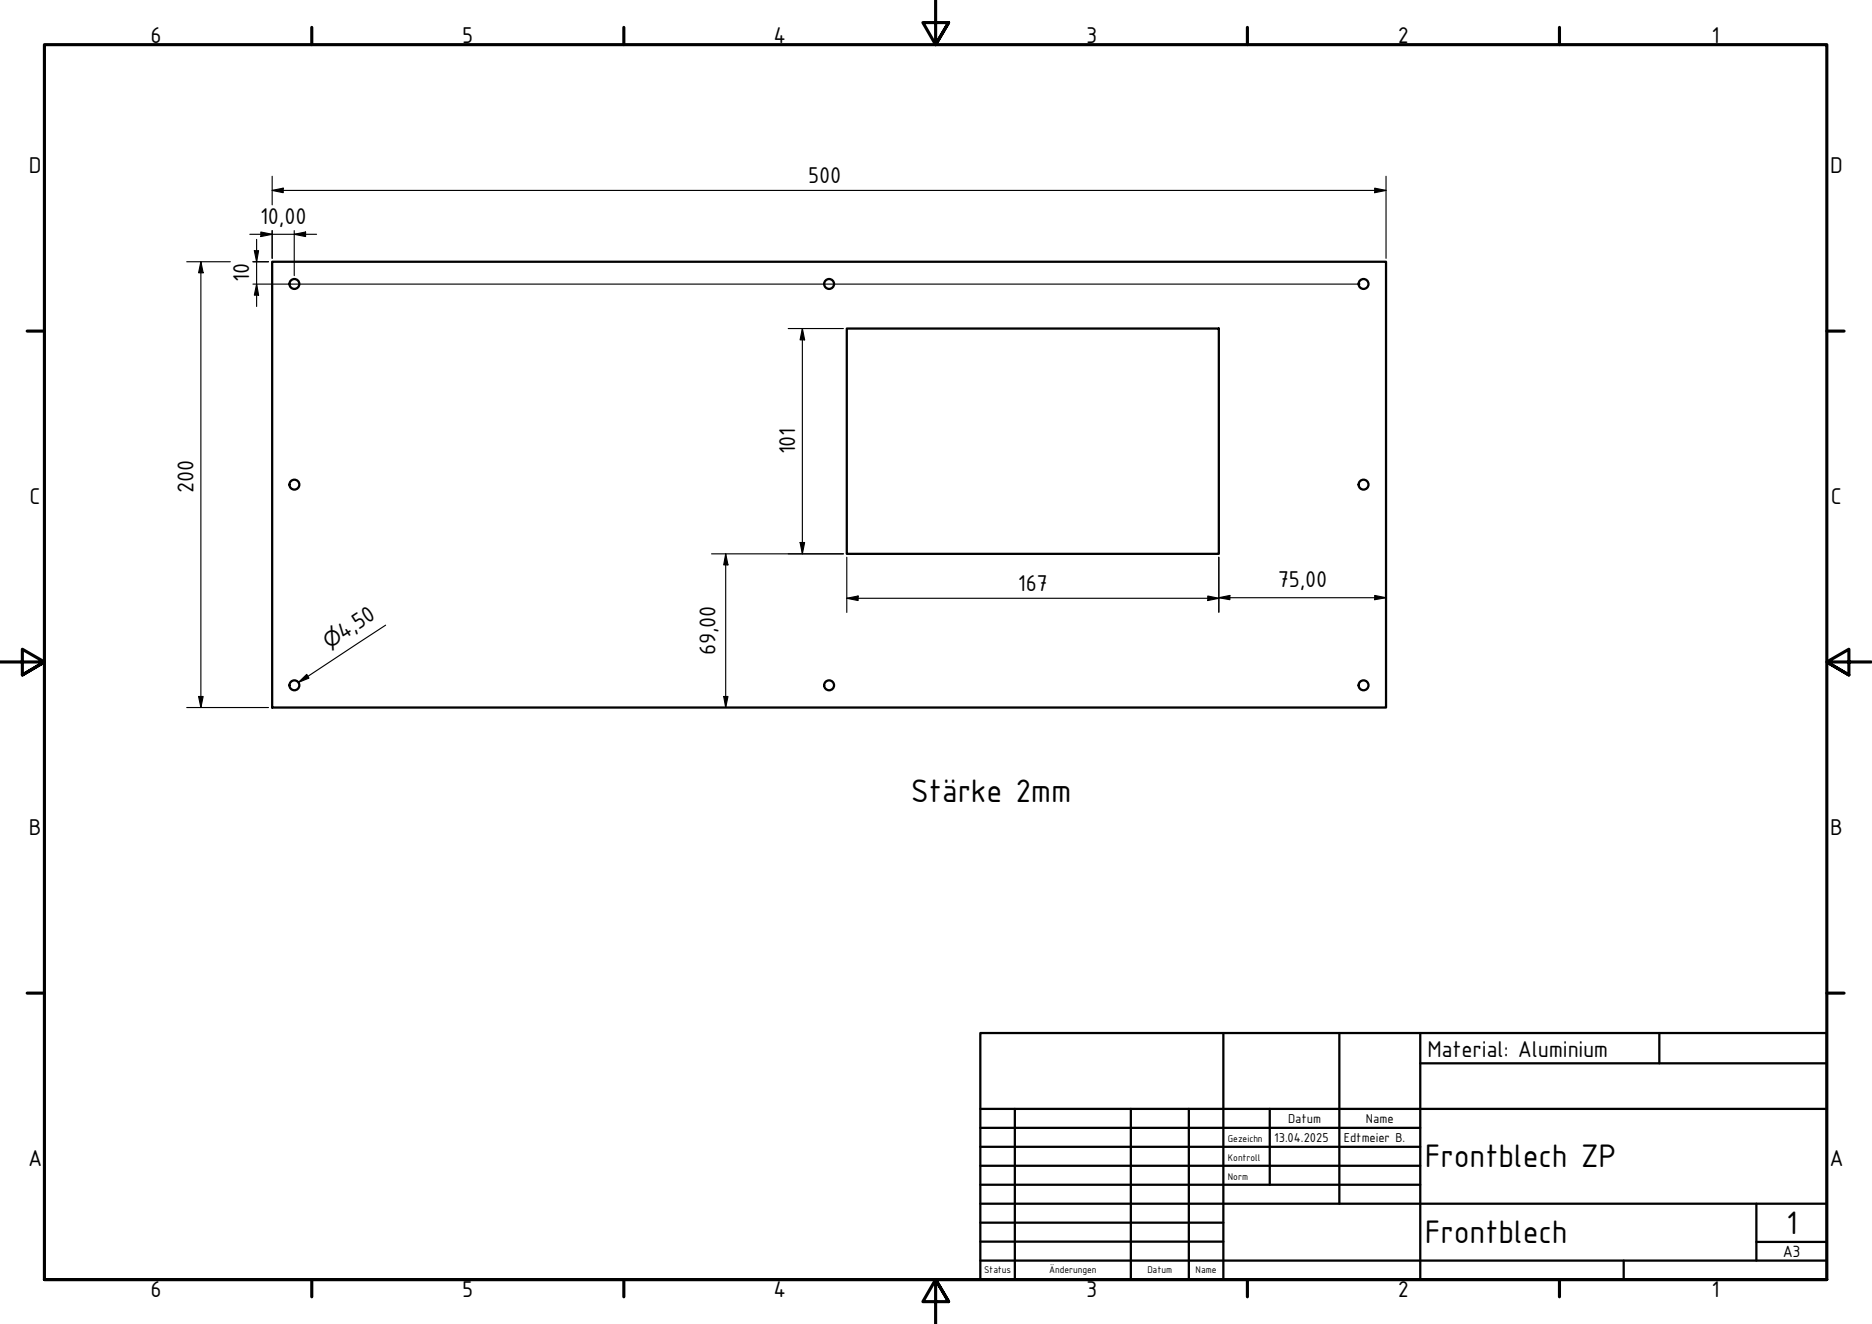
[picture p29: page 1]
Material: Aluminium

Datum | Name | Frontblech ZP

Gezeichn | 13.04.2025 | Edtmeier B.

Kontroll

Norm

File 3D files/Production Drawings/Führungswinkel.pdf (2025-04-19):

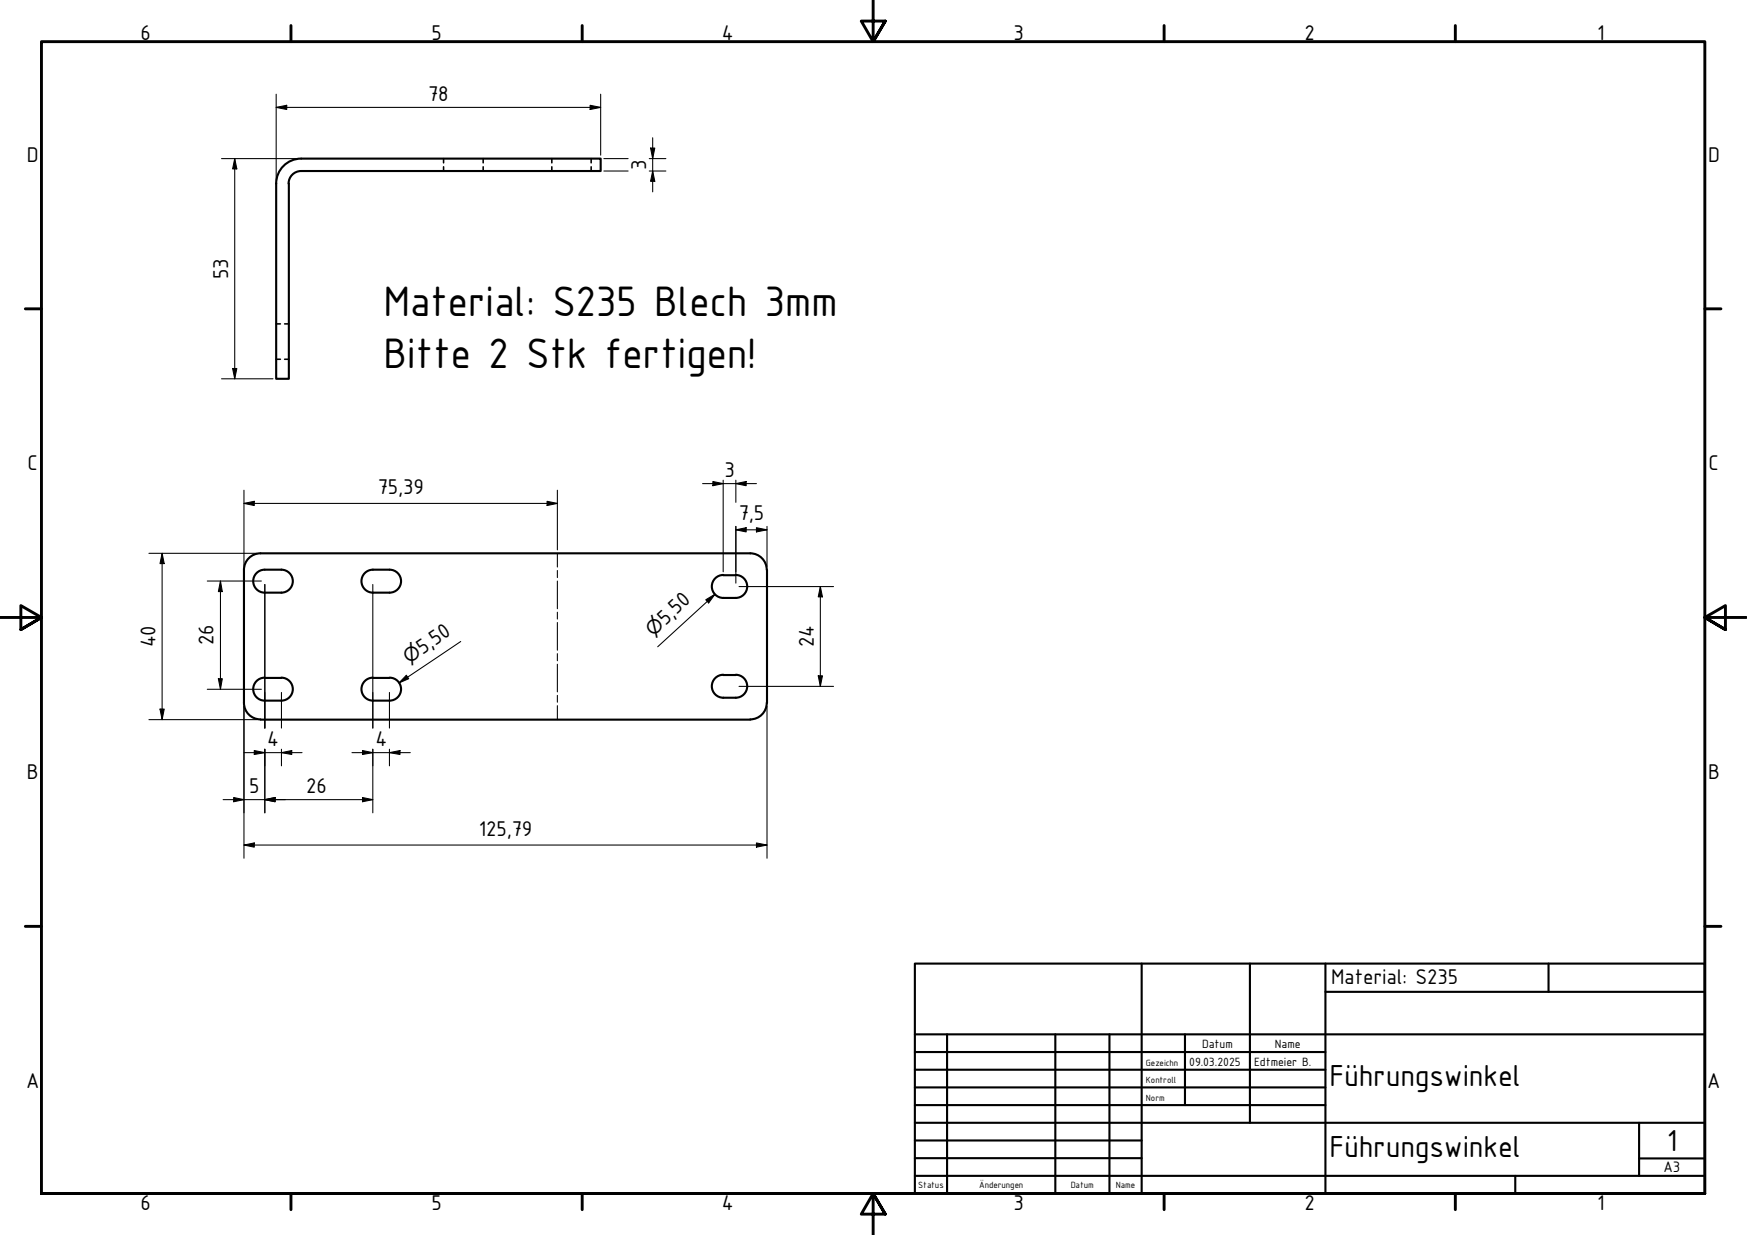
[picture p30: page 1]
Material: S235

Material: S235 Blech 3mm
Bitte 2 Stk fertigen!

Datum | Name | F¯hrungswinkel

Gezeichn | 09.03.2025 | Edtmeier B.

Kontroll

Norm

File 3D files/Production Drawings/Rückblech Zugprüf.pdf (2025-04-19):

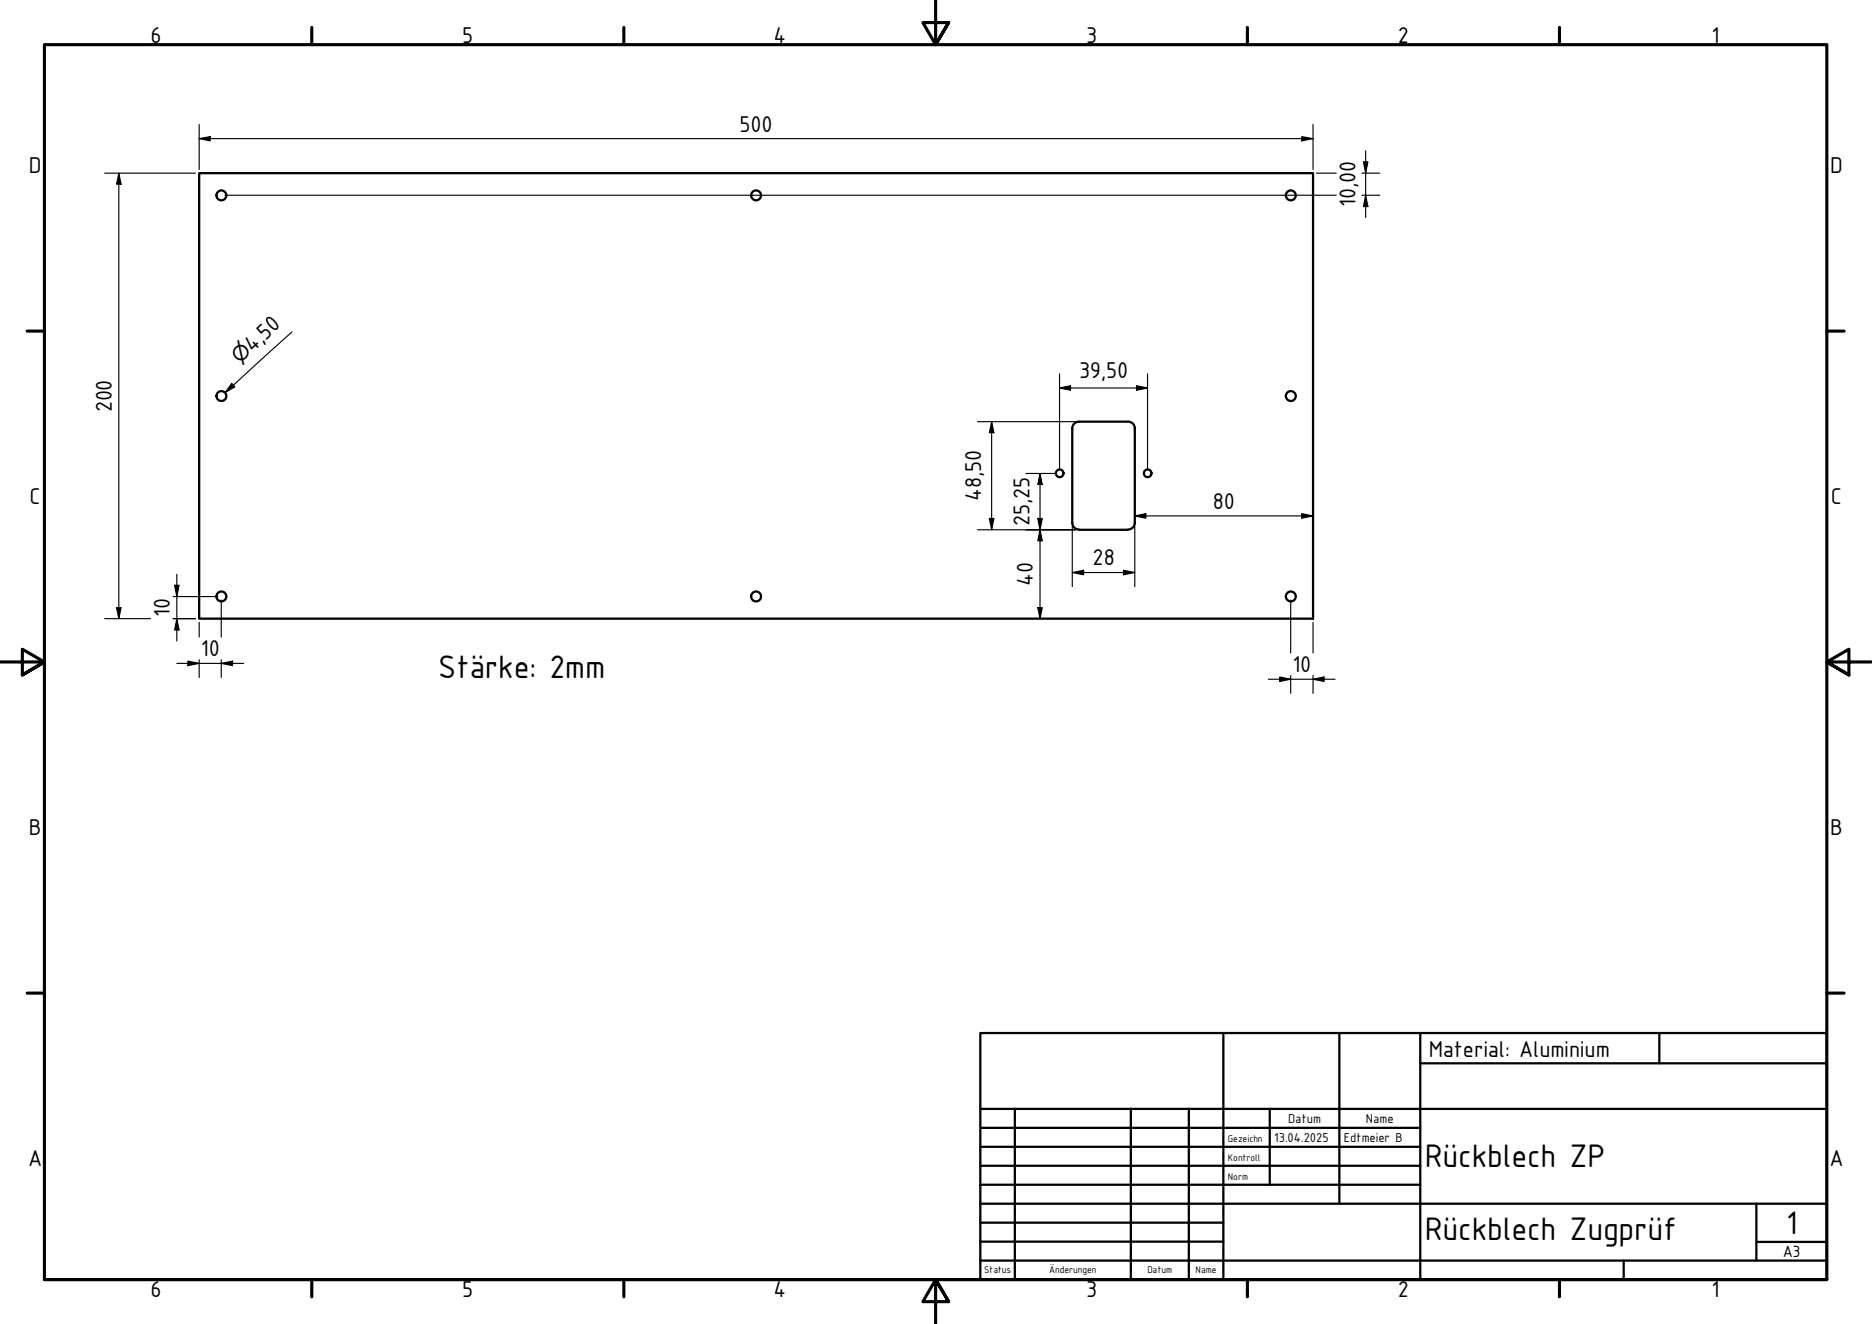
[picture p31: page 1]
R¯ckblech Zugpr¯f; Material: Aluminium

Datum | Name | R¯ckblech ZP

Gezeichn | 13.04.2025 | Edtmeier B

Kontroll

Norm

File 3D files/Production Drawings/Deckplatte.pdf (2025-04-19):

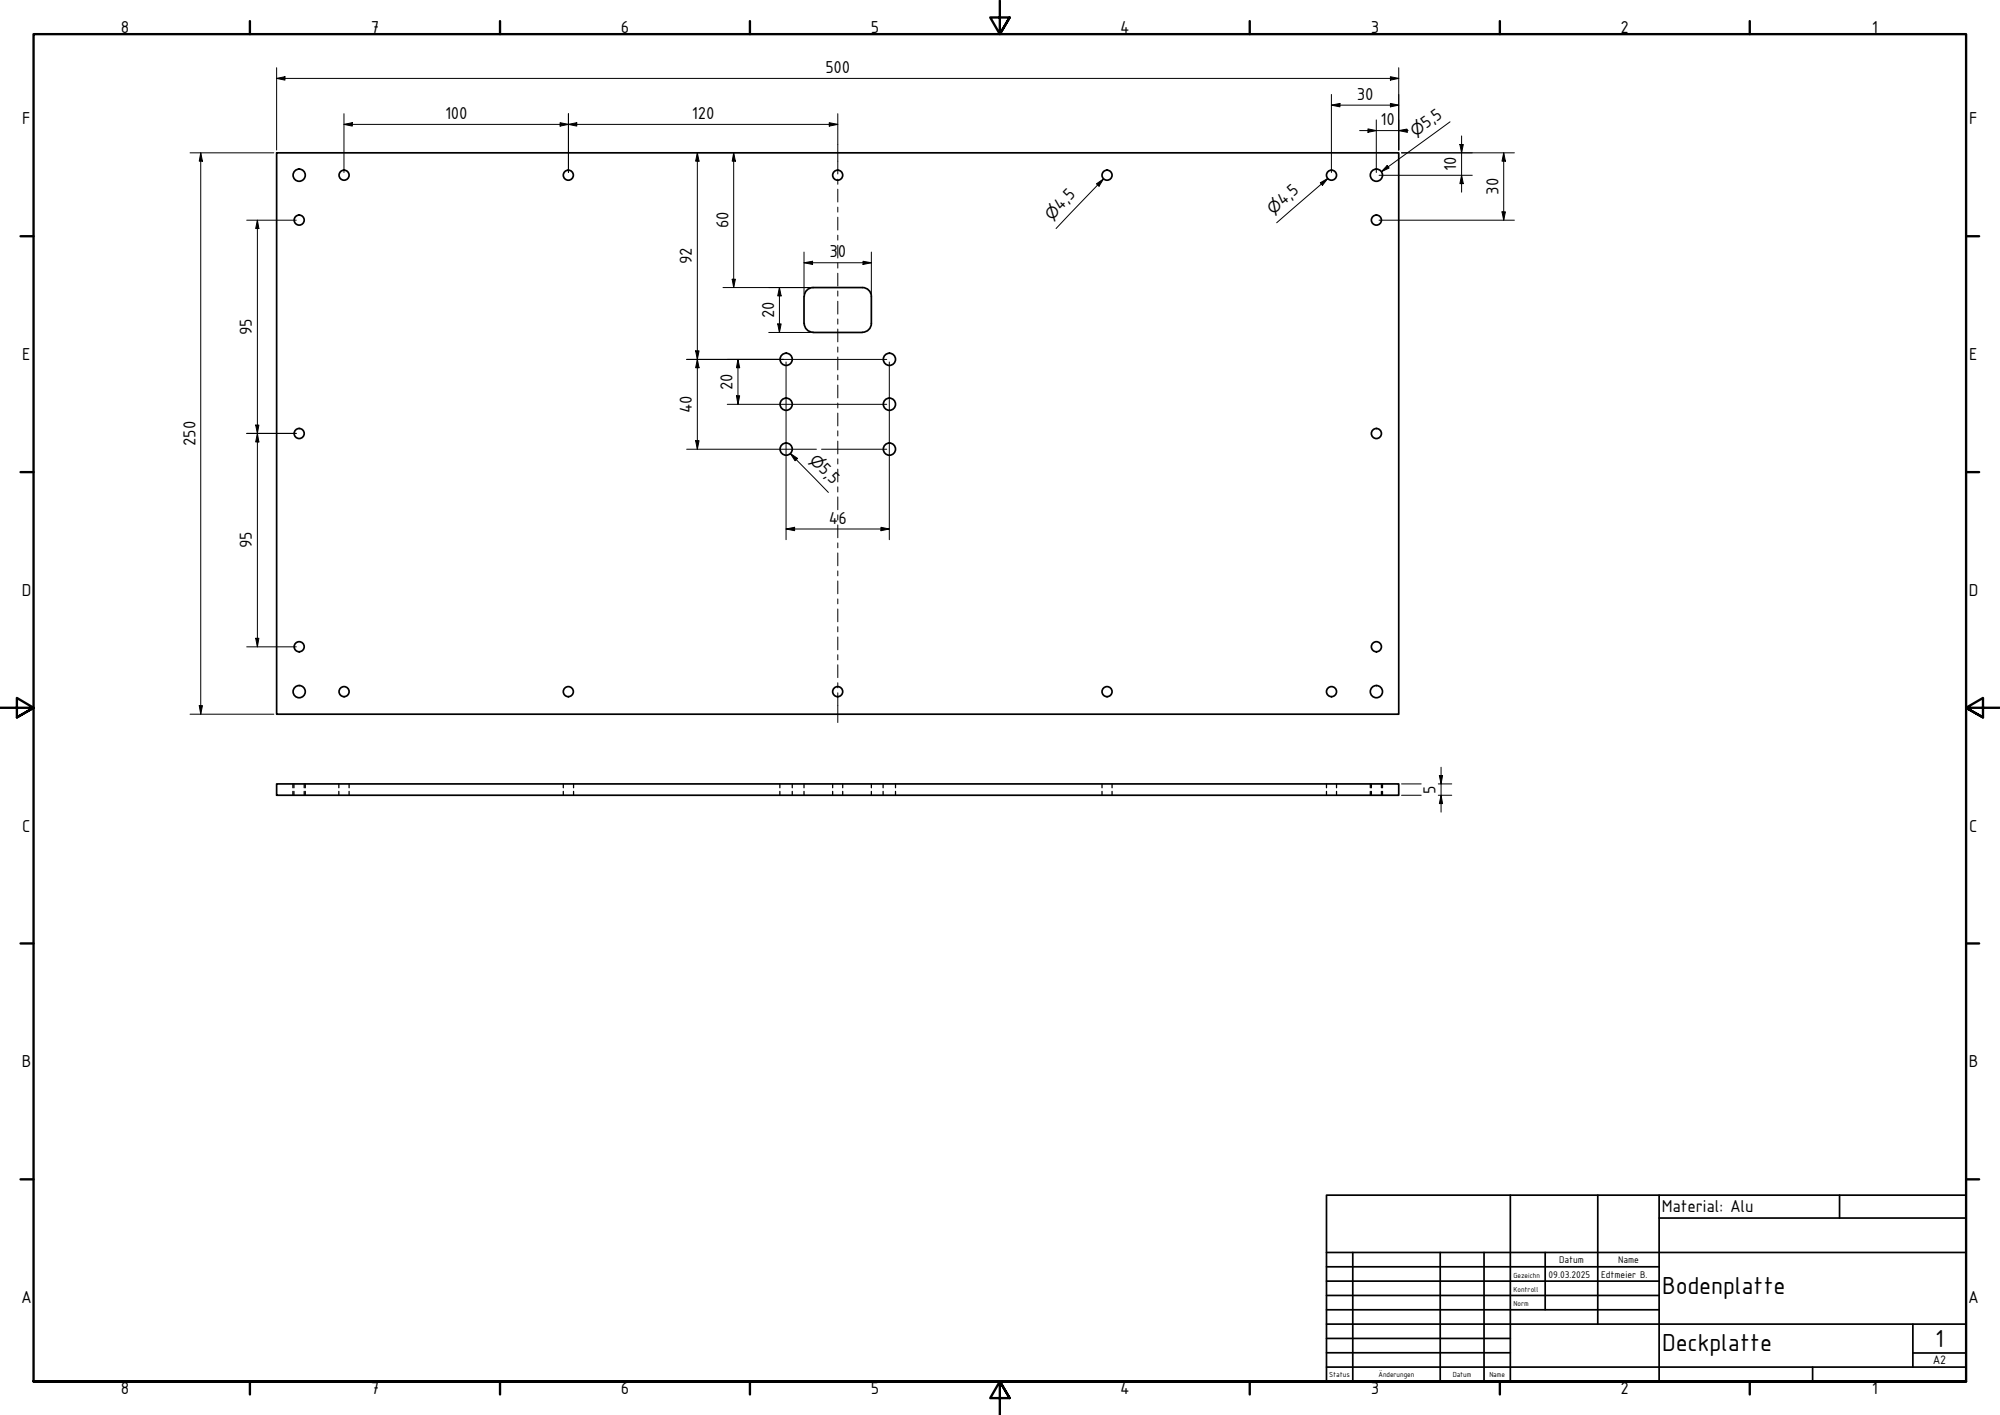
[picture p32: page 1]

G e z eic h n | 0 9.0 3.2 0 2 5 | E d t m eie r

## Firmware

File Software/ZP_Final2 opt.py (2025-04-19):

import ttkbootstrap as ttk
from ttkbootstrap.constants import *
import tkinter as tk
import sys
import threading
import time
import os
from HX711 import HX711
from gpiozero import PWMOutputDevice, DigitalOutputDevice


class ZugpruefmaschineGUI:
    def __init__(self, root):
        self.root = root
        self.root.attributes('-fullscreen', True)
        self.root.title("Zugprüfmaschine Touch-Steuerung")

        # ------------------------------------------
        # 1) Initialisierung HX711
        # ------------------------------------------
        self.hx = HX711(dout_pin=5, sck_pin=6, reference_unit=420.0, readings=1)
        self.hx.tare()

        # Kraftanzeige-Variablen
        self.current_force = 0.0
        self.force_value_var = tk.StringVar(value="Kraft: 0.00 N")
        self.max_force_value = 0.0
        self.max_force_var = tk.StringVar(value="Max: 0.00 N")

        # Für den Filter:
        self.last_valid_force = None
        self.candidate_count = 0
        self.candidate_sum = 0.0

        # ------------------------------------------
        # 2) Initialisierung Schrittmotor
        # ------------------------------------------
        self.step_pin = 18
        self.dir_pin = 19
        self.enable_pin = 26
        self.step = DigitalOutputDevice(self.step_pin, active_high=True, initial_value=False)
        self.dir = DigitalOutputDevice(self.dir_pin, active_high=True, initial_value=False)
        self.enable = DigitalOutputDevice(self.enable_pin, active_high=True, initial_value=False)

        self.steps_per_rev = 1600
        self.rotation_distance = 3.125  # mm pro Umdrehung
        self.position = 0.0             # Aktuelle Position in mm

        # ------------------------------------------
        # 3) Variablen für Kraftabfall, Zuglänge, Vorschub, Logfile
        # ------------------------------------------
        self.kraft_abfall_grenze = 0
        self.zuglaenge = 5
        self.feed_rate = 5

        # Logbase-Name (wird über das GUI-Entry gesetzt)
        self.log_base_var = tk.StringVar(value="zugversuch_log")

        # Prozess-Flags
        self.is_testing = False
        self.process_stop_event = threading.Event()
        self.process_thread = None

        # GUI aufbauen
        self.build_layout()

        # ------------------------------------------
        # 4) Sensor-Thread: Liest den HX711 alle 0.1 s (10 Hz)
        # ------------------------------------------
        self.stop_event = threading.Event()
        self.sensor_thread = threading.Thread(target=self.update_force_loop, daemon=True)
        self.sensor_thread.start()

    # Neue Methode: Ausfallsicheres Auslesen mittels Timeout, das auf das Signal des HX711 wartet
    def read_value_with_timeout(self, timeout_ms=15):
        start_time = time.perf_counter()  # Startzeit in Sekunden
        timeout_sec = timeout_ms / 1000.0  # Timeout in Sekunden
        # Warte darauf, dass der DOUT-Pin signalisiert, dass ein neuer Wert vorliegt (also LOW)
        while self.hx.dout.value:
            if (time.perf_counter() - start_time) > timeout_sec:
                return None
        return self.hx.get_value()

    # Filterfunktion: Verarbeitet einen neuen Kraftwert anhand des zuletzt akzeptierten Wertes.
    # Bei einem plötzlichen Sprung über den Schwellenwert (15 N) wird der neue Wert als Kandidat registriert.
    # Liegen zwei aufeinanderfolgende Kandidaten innerhalb einer Toleranz von 2 N, wird der Übergang akzeptiert.
    def filter_force(self, new_val, threshold=15.0, tolerance=2.0):
        if self.last_valid_force is None:
            self.last_valid_force = new_val
            self.candidate_count = 0
            self.candidate_sum = 0.0
            return new_val
        # Wenn die Differenz zum letzten gültigen Wert innerhalb des Schwellenwerts liegt, sofort übernehmen.
        if abs(new_val - self.last_valid_force) <= threshold:
            self.candidate_count = 0
            self.candidate_sum = 0.0
            self.last_valid_force = new_val
            return new_val
        else:
            # Neuer Messwert unterscheidet sich deutlich vom letzten gültigen.
            if self.candidate_count == 0:
                # Ersten Kandidaten speichern und alten Wert anzeigen.
                self.candidate_count = 1
                self.candidate_sum = new_val
                return self.last_valid_force
            elif self.candidate_count == 1:
                # Zweiter Kandidat: Prüfen, ob beide Kandidaten innerhalb der Toleranz liegen.
                if abs(new_val - self.candidate_sum) <= tolerance:
                    # Übergang akzeptieren: Mittelwert der Kandidaten berechnen.
                    filtered = (self.candidate_sum + new_val) / 2.0
                    self.last_valid_force = filtered
                    self.candidate_count = 0
                    self.candidate_sum = 0.0
                    return filtered
                else:
                    # Kandidaten nicht konsistent: Ausreißer verwerfen, alten Wert beibehalten.
                    self.candidate_count = 0
                    self.candidate_sum = 0.0
                    return self.last_valid_force

    # ------------------------------------------
    # GUI Layout
    # ------------------------------------------
    def build_layout(self):
        frame = ttk.Frame(self.root, padding=20)
        frame.pack(fill='both', expand=True)

        # Oberer Bereich: Position, Kraft, Max-Kraft
        display_frame = ttk.Frame(frame)
        display_frame.pack(fill='x', pady=10)

        self.pos_display = ttk.Label(display_frame, text="Position: 0.00 mm", font=("Helvetica", 24))
        self.pos_display.pack(side='left', padx=40)

        self.force_value = ttk.Label(display_frame, textvariable=self.force_value_var, font=("Helvetica", 24))
        self.force_value.pack(side='left', padx=40)

        self.max_force_label = ttk.Label(display_frame, textvariable=self.max_force_var, font=("Helvetica", 24))
        self.max_force_label.pack(side='left', padx=40)

        # Mittlerer Bereich: Position steuern und Zuglänge einstellen
        control_row = ttk.Frame(frame)
        control_row.pack(fill='x', pady=10)

        # Position steuern Frame
        pos_frame = ttk.LabelFrame(control_row, text="Position steuern", padding=20)
        pos_frame.pack(side='left', fill='both', expand=True, padx=10)

        pos_btn_frame = ttk.Frame(pos_frame)
        pos_btn_frame.pack()

        for step in [-10, -1, -0.5, 0.5, 1, 10]:
            style = PRIMARY
            label = f"{step:+}".replace(".0", "") + " mm"
            ttk.Button(pos_btn_frame, text=label, bootstyle=style, width=10,
                       command=lambda s=step: self.move_by(s)).pack(side='left', padx=5)

        # Zuglänge einstellen Frame
        zug_frame = ttk.LabelFrame(control_row, text="Zuglänge", padding=20)
        zug_frame.pack(side='left', fill='both', expand=True, padx=10)

        self.zuglaenge_label = ttk.Label(zug_frame, text=f"{self.zuglaenge} mm", font=("Helvetica", 24))
        self.zuglaenge_label.pack(pady=10)

        zug_btn_frame = ttk.Frame(zug_frame)
        zug_btn_frame.pack()

        ttk.Button(zug_btn_frame, text="-1 mm", bootstyle=PRIMARY, width=7,
                   command=lambda: self.adjust_zuglaenge(-1)).pack(side='left', padx=5)
        ttk.Button(zug_btn_frame, text="+1 mm", bootstyle=PRIMARY, width=7,
                   command=lambda: self.adjust_zuglaenge(1)).pack(side='left', padx=5)

        # Vorschub- und Kraftabfall-Bereiche
        feed_kraft_frame = ttk.Frame(frame)
        feed_kraft_frame.pack(fill='x', pady=10)

        # Vorschubsteuerung
        feed_frame = ttk.LabelFrame(feed_kraft_frame, text="Vorschub verstellen", padding=20)
        feed_frame.pack(side='left', fill='x', expand=True, padx=10)

        self.feed_display = ttk.Label(feed_frame, text=f"Vorschub: {self.feed_rate} mm/min", font=("Helvetica", 24))
        self.feed_display.pack(pady=10)

        feed_btn_frame = ttk.Frame(feed_frame)
        feed_btn_frame.pack()

        for step in [-10, -1, 1, 10]:
            style = PRIMARY
            label = f"{step:+}".replace(".0", "") + " mm/min"
            ttk.Button(feed_btn_frame, text=label, bootstyle=style, width=12,
                       command=lambda s=step: self.adjust_feed(s)).pack(side='left', padx=5)

        # Kraftabfall-Grenze
        kraft_frame = ttk.LabelFrame(feed_kraft_frame, text="Kraftabfall-Grenze", padding=20)
        kraft_frame.pack(side='left', fill='x', expand=True, padx=10)

        self.kraft_display = ttk.Label(kraft_frame, text=f"Grenze: {self.kraft_abfall_grenze} N", font=("Helvetica", 24))
        self.kraft_display.pack(pady=10)

        kraft_btn_frame = ttk.Frame(kraft_frame)
        kraft_btn_frame.pack()

        for delta in [-5, 5]:
            label = f"{delta:+} N"
            ttk.Button(kraft_btn_frame, text=label, bootstyle=PRIMARY, width=10,
                       command=lambda d=delta: self.adjust_kraft_grenze(d)).pack(side='left', padx=10)

        # Unterer Bereich: Tarieren und Log-Base Eingabe
        control_frame = ttk.Frame(frame)
        control_frame.pack(fill='x', pady=15)

        ttk.Button(control_frame, text="Tarieren", bootstyle=WARNING, width=10,
                   command=self.tare).pack(side='left', padx=10)

        log_base_frame = ttk.Frame(control_frame)
        log_base_frame.pack(side='right', padx=10)
        ttk.Label(log_base_frame, text="Log-Base:", font=("Helvetica", 14)).pack(side='left', padx=5)
        self.log_base_entry = ttk.Entry(log_base_frame, textvariable=self.log_base_var, width=20)
        self.log_base_entry.pack(side='left', padx=5)

        # Prozessbereich
        process_frame = ttk.Frame(frame)
        process_frame.pack(fill='x', pady=20)

        self.start_button = ttk.Button(process_frame, text="Prozess starten", bootstyle=SUCCESS, width=20,
                                        command=self.toggle_process)
        self.start_button.pack(side='left', padx=10)

        ttk.Button(process_frame, text="Pos. Nullsetzen", bootstyle=PRIMARY, width=16,
                   command=self.reset_position).pack(side='left', padx=10)

        ttk.Button(process_frame, text="Zurück zu 0 Position", bootstyle=WARNING, width=18,
                   command=self.return_to_zero).pack(side='left', padx=10)

        self.logfile_label = ttk.Label(process_frame, text="", font=("Helvetica", 14))
        self.logfile_label.pack(side='left', padx=20)

        ttk.Button(process_frame, text="Beenden", bootstyle=DANGER, width=12,
                   command=self.exit_app).pack(side='right', padx=20)

    # ------------------------------------------
    # Sensor-Thread: Liest den HX711 alle 0.1 s (10 Hz) und wendet den Filter an
    # ------------------------------------------
    def update_force_loop(self):
        sample_interval = 0.0125  # in Sekunden (10 Hz)
        while not self.stop_event.is_set():
            loop_start = time.perf_counter()
            raw_value = self.read_value_with_timeout(timeout_ms=15)
            if raw_value is not None:
                force = raw_value * -0.0003024406
                # Filterung: neuer Wert wird durch den Filter verarbeitet.
                filtered_force = self.filter_force(force)
                self.current_force = filtered_force
                self.force_value_var.set(f"Kraft: {filtered_force:.2f} N")
                if filtered_force > self.max_force_value:
                    self.max_force_value = filtered_force
                    self.max_force_var.set(f"Max: {self.max_force_value:.2f} N")
            elapsed = time.perf_counter() - loop_start
            if elapsed < sample_interval:
                time.sleep(sample_interval - elapsed)
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

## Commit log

2025-04-19 First upload
    [Stückliste Minizugprüf Eddi.xlsx]
2025-04-19 added STL data for 3D printing
    [Auflage Kabelschlepp.stl, Bildschirm Halterung.stl, Bildschirm Steher.3mf, Bildschirm Steher.stl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]
2025-04-27 Addition sample typ CW
    [sample Typ CW.3mf, sample Typ CW.stl]
2025-04-27 Update README sample addition
2025-05-10 milled sample holder
    [Sample Holder flying CW.stp, Sample holder fixed CW.stp]
